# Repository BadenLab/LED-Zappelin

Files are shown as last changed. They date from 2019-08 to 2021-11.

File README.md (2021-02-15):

<p align="right">
<h1 align="center">LED Zappelin'</h1></p>
<h3 align="center">An open source and versatile LED controller for arbitrary spectrum visual stimulation<br>
and optogenetics during 2-photon imaging.</h4>
<p align="center"><h6 align="right">by M.J.Y. Zimmermann, A.M. Chagas, P. Bartel, S. Pop, L.L. Prieto Godino & T. Baden</h6></p>

<br>

This project was published in July 2020 in the journal [HardwareX](https://www.sciencedirect.com/science/article/pii/S2468067220300365)<br>
This project is licensed under the [GNU General Public License v3.0](https://github.com/BadenLab/LED-Zappelin/blob/master/LICENSE)<br>
The hardware is licensed under the [CERN OHL v1.2](https://github.com/BadenLab/LED-Zappelin/blob/master/PCB/LICENSE)

Demo CountPages alpha (https://youtu.be/FhLoFGbbpPo)

***

<h4 align="justify"> Two-photon (2P) microscopy is a cornerstone technique in neuroscience research, but combining this technology with spectrally arbitrary light stimulation can be challenging due to crosstalk between stimulation light and fluorescence detection. To overcome this limitation, we present a simple and low-cost electronic solution based on an ESP32 microcontroller and a TLC5947 LED driver to rapidly time-interleave stimulation and detection epochs during scans. Implemented for less than $100, our design can independently drive up to 24 arbitrary spectrum LEDs to meet user requirements. We demonstrate the utility of our stimulator for colour vision experiments on the in vivo tetrachromatic zebrafish retina and for optogenetic circuit mapping in Drosophila.</h4></p>

***

- [An open and versatile LED controler](#Introduction)
- [A £100 DIY efficient stimulator](https://github.com/BadenLab/LED-Zappelin/blob/master/Bills%20of%20Materials/BOM%20-%20Stimulator.csv)
- [A stimulator for visual neuroscience](#Colour-Vision-Experiment)
- [A stimulator for optogenetics](#Optogenetics-Experiment)
- [A detailed assembly and instruction manual](https://github.com/BadenLab/LED-Zappelin/blob/master/Instruction%20Manual/README.md)
- [A step by step calibration script](https://github.com/BadenLab/LED-Zappelin/blob/master/Instruction%20Manual/Stimulator%20Calibration/Stimulator_Calibration.ipynb)
- [Repository Structure](#Repository-Structure)

***

## Introduction

<p align="justify"> Combining 2P imaging with additional light stimulation – for example for visual stimulation or for driving optogenetic actuators – has remained challenging because the stimulation light can interfere with fluorescence detection. This can result in light artefacts in the image and/or may damage sensitive fluorescence detection equipment (e.g. photomultiplier tubes, PMTs).</p>

<p align="justify">A temporal separation between light stimulation and fluorescence detection, for example during the scan-retrace, can ameliorate these problems.
This problem can be readily solved electronically, for example through use of a microcontroller.</p>

<p align="justify">Here, we present such a solution. Our system can line-synch up to 24 independent LED channels, and can be assembled from off-the-shelf components for substantially below $100. This provides for flexible options of spectrally diverse light stimulation during 2-photon scanning and comfortably provides sufficient power to drive standard optogenetics actuators such as CsChrimson.</p>

<p align="justify">Alongside, we also provided a custom 3D-printed casing, designed suggestions for optically combining LED banks using Thorlabs parts, and an alternative 3D-printed LED holder and microscope chamber. For software control, we provided custom Arduino scripts to flexibly programme stimulation protocols.</p>

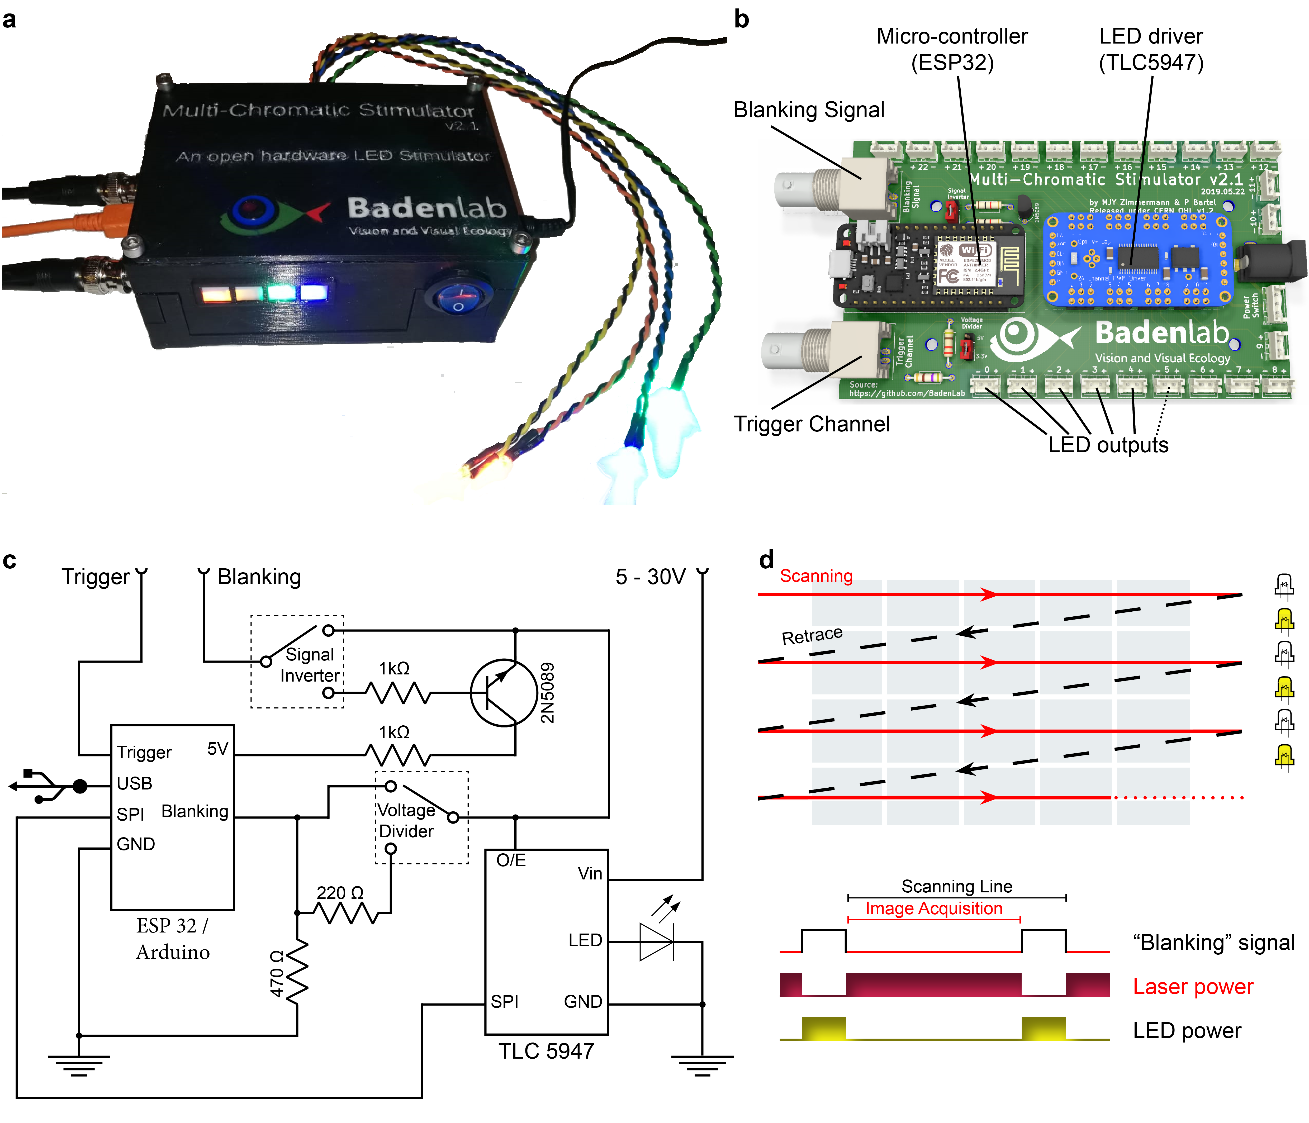
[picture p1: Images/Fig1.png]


<h5 align="justify"> a) A fully assembled stimulator. b) Rendering of the custom-printed circuit board which accommodates the microcontroller, the LED driver and up to 24 LED channels. c) Schematics illustrating the circuit that controls the LED output. The blanking input can be inverted by a switch before reaching the output enable pin on the LED driver (electronically switching off the LEDs) and sending the signal to the micro-controller. A second switch control the blanking signal voltage as it needs to be adapted depending on the logic of the microcontroller used (3.3V for ESP32, 5V for Arduino). The microcontroller controls the LED driver through an SPI connection and send trigger signal output to an external. d) Illustration of the raster scan method described. The “blanking signal” is synchronous with the scanning logic, enabling the LEDs during the scanning mirrors retrace (black) and shutting them off during the acquisition (red), therefore providing temporal separation between stimulation and detection (Modified from (Euler et al. 2019)</h5>

***

<p align="justify">The stimulator runs synchronous to the recording system using TTL triggers. TTL signals correspond to scanning mirror retrace periods and are used to turn ON and OFF LEDs, thus avoiding swamping the PMTs by stimulation light.

<p align="justify">On the PCB, we incorporated a signal inverter which can be enabled through a jumper (see below) and that can modulated the TTL signal sign. This customisable option thus offers the possibility for a single design to be easily adapted to multiple imaging systems.</p>

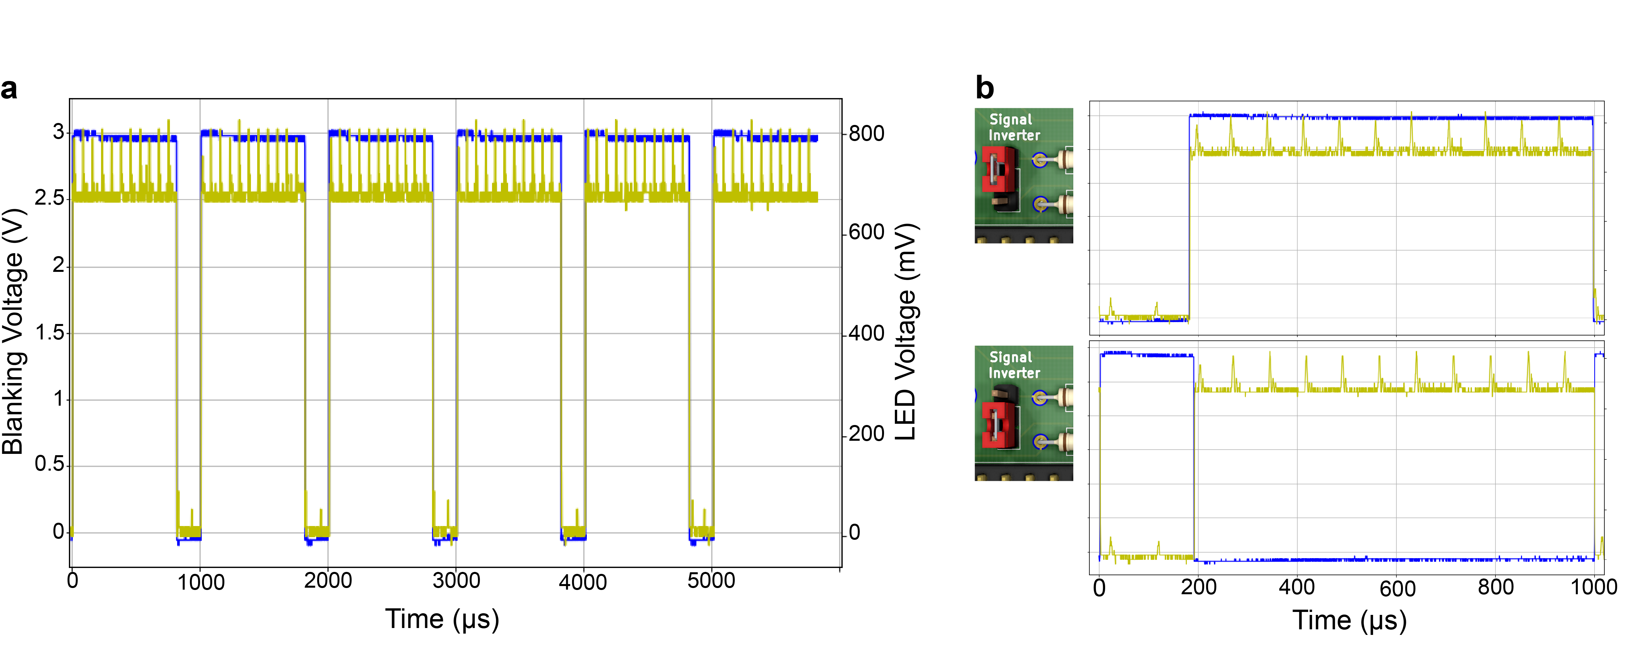
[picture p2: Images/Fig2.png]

<h5 align="justify"> a) Oscilloscope reading of the blanking signal (blue) efficiently switching off an LED (yellow). The blanking is operated here without noticeable delay. b) Same as a), showing for a 1ms scanning cycle, the two possible configurations for the blanking signal input, with a low (top) and a high (bottom) blanking signal input respectively for an inverted and original signal input. </h5>

***

<p align="justify"> The use of a dedicated constant current LED driver tends to improve LED stability over time as well as its life span. Such driver ensures that the current drawn by the LED never leads to thermal runaways that might cause irreversible damage. This is particularly essential for short wavelength LEDs which tend to rapidly decay, thus necessitating regular recalibration or replacement. </p>

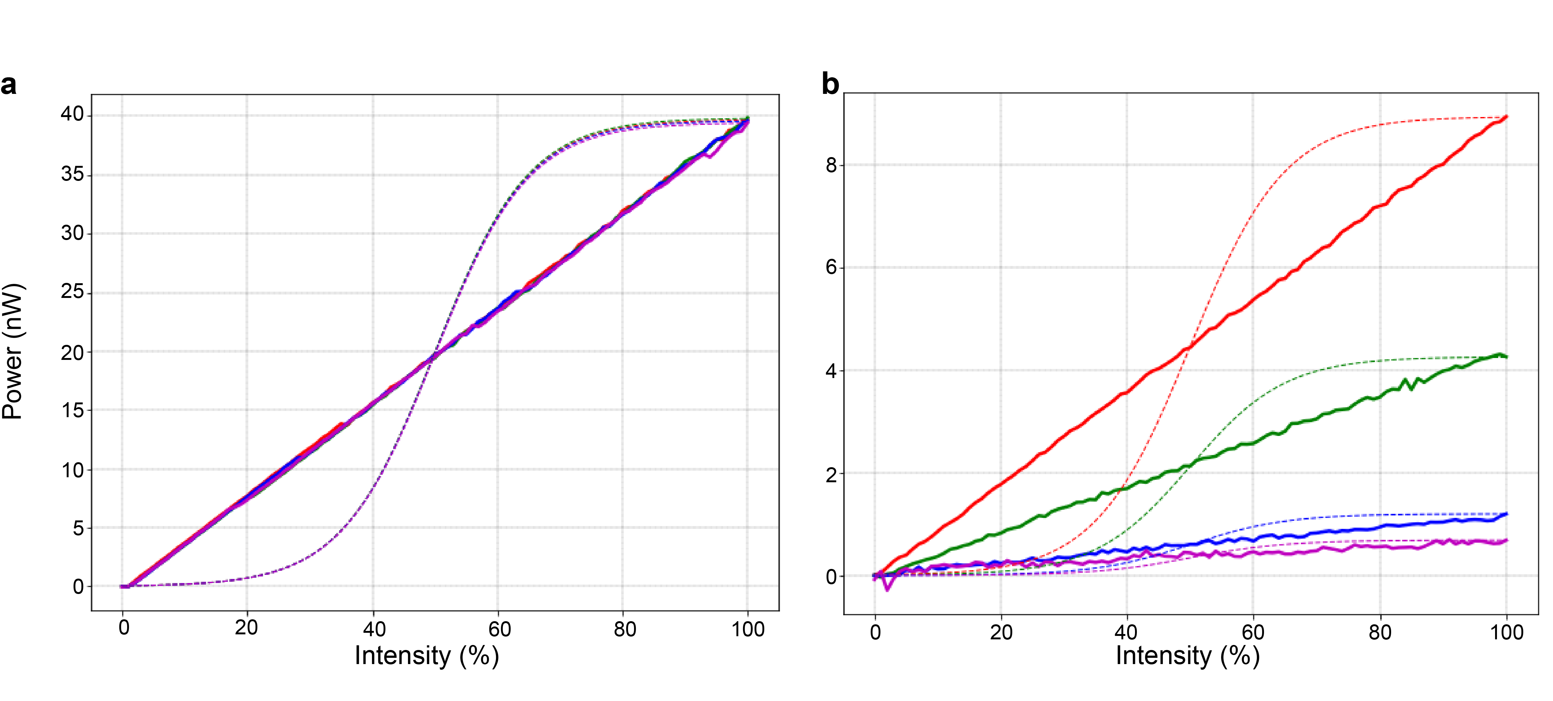
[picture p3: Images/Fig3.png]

<h5 align="justify">  a) Power recording of a 4 LED system using the TLC5947 (solid lines) and their expected brightness if directly controlled by a microcontroller (dashed lines). All LEDs have been set up to the same power (40nW), with equal max intensities values in the Arduino code. b) Same as a) but with LEDs set up at different max intensities in the Arduino code. Here the linearity of the LED intensity output remains constant. </5>

***

## Colour Vision Experiment

<p align="justify">We used LED Zappelin' for studying the retinal processing of the tetrachromatic zebrafish retina in response to multichromatic signal.
Here we selected four LEDs that match the peak sensitivities of each cone opsins of our model.
We chose LEDs and band pass filters in such manner that the stimulating light and the detection bands do not overlap as much as possible. However a temporal separation is still necessary to avoid some overlapping and any light artifact. </p>

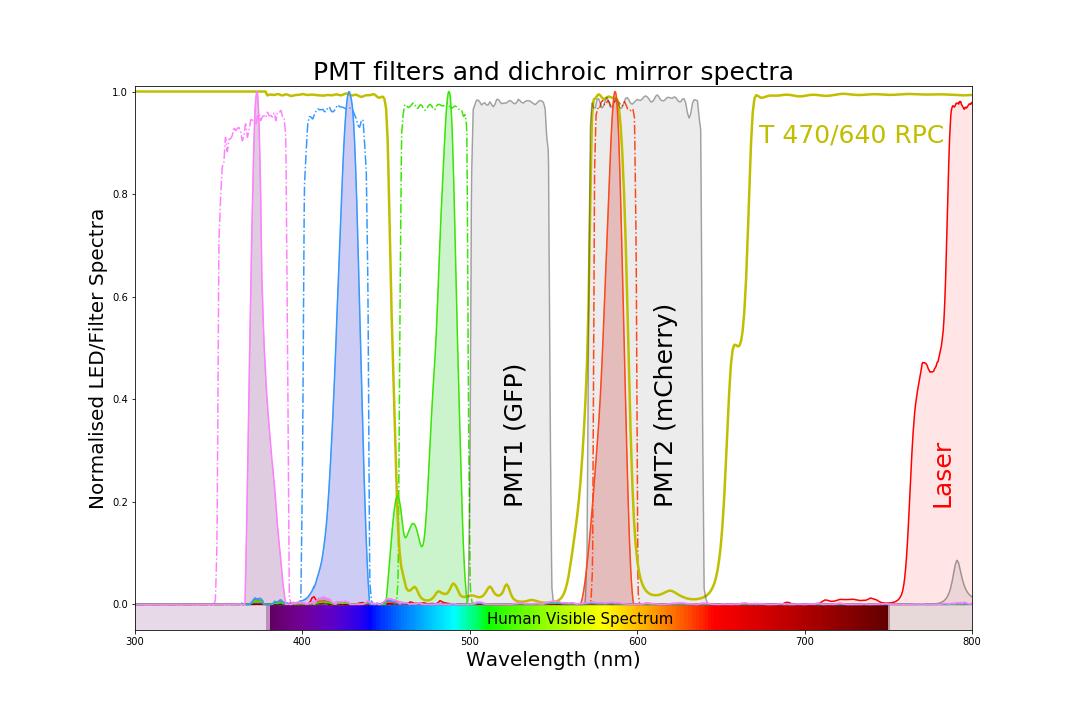
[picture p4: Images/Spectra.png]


 We recorded light-driven calcium signals under 2-photon from [retinal bipolar cells in vivo in the tetrachromatic larval zebrafish](https://github.com/BadenLab/LED-Zappelin/blob/master/References/Zimmermann%202018%20-%20Zebrafish%20Differentially%20Procces%20Colour%20across%20Visual%20Space%20to%20Match%20Natural%20Scenes.pdf). We used a transgenic line expressing a genetically encoded biosensors for calcium at the  bipolar cell synaptic terminals level (ctbp2:SyGCaMP6)  within the inner plexiform layer (IPL).

Following [established protocols](https://github.com/BadenLab/LED-Zappelin/blob/master/References/Denk%202009%20-%20Eyecup%20Scope%20-%20optical%20recordings%20of%20light%20stimulus-evoked%20fluorescence%20signals%20in%20the%20retina.pdf), we used a Sutter MOM microscope where light stimulation is displayed through the objective directly onto the fish retina along with the laser excitation. Fluorescence is also collected through the objective as well as from below the stage (not shown).

We presented full field steps of red, green, blue and UV light to the fish eye (respectively 567, 480, 420 and 365nm), and recorded evoked calcium signals as a readout of synaptic activity. We observed spectrally different tunings from distinct bipolar cell terminals  without detectable stimulus artefact across the scan.

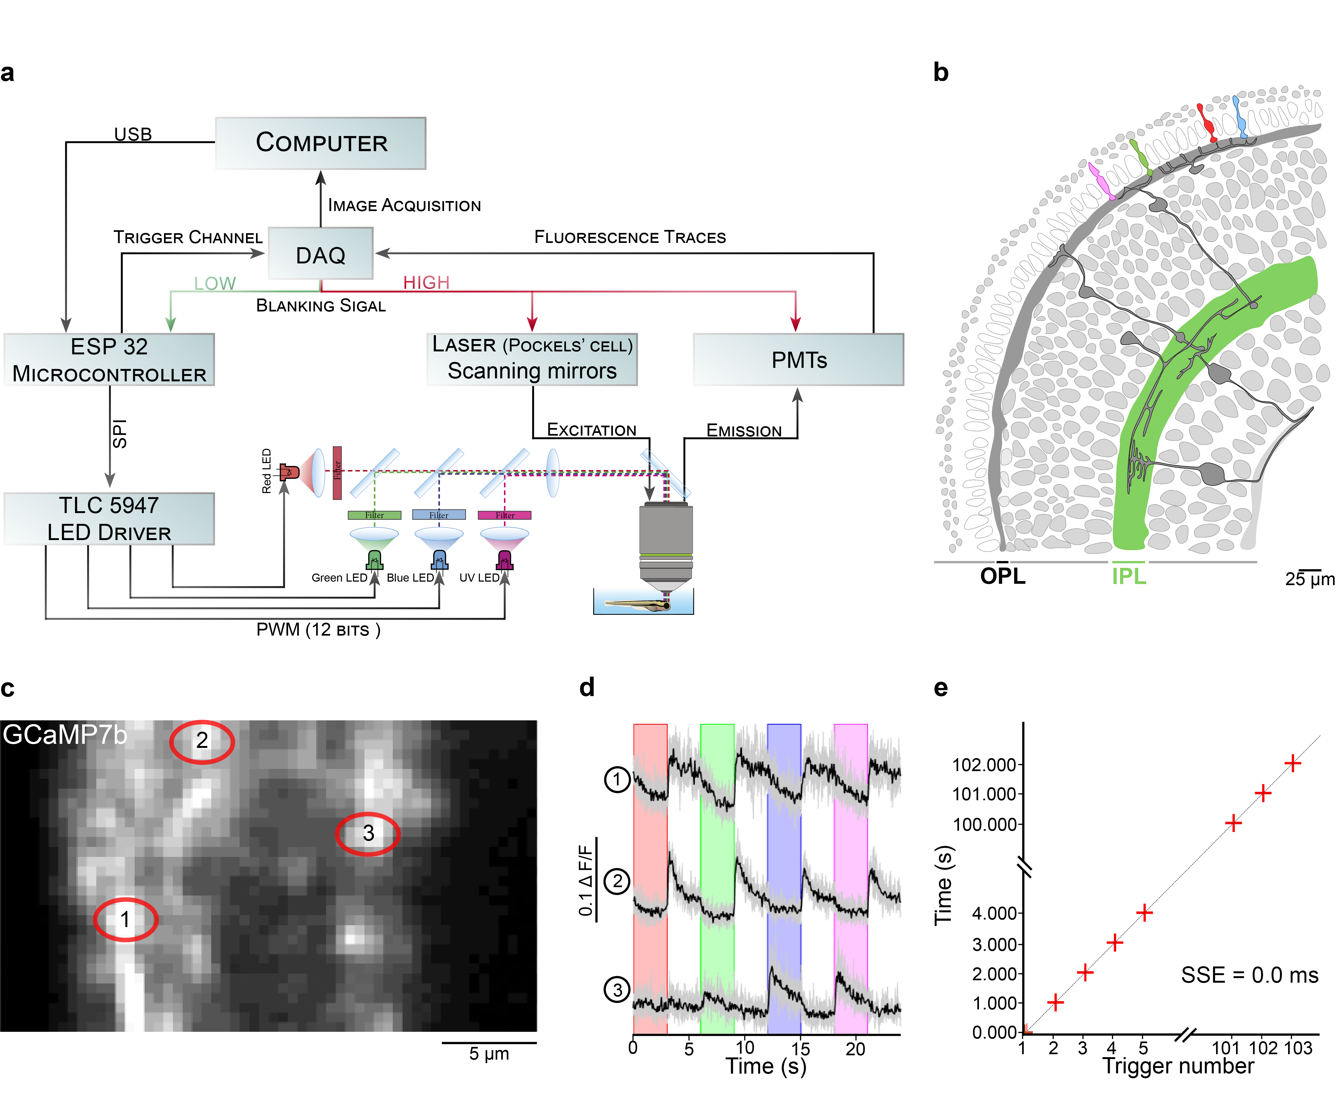
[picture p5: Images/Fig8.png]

<h5 align="justify"> a) Overview of the setup described for the visual stimulation experiment performed on the tetrachromatic zebrafish. b) Drawing of the larval zebrafish retina highlighting the IPL. c) 2 photon scan field of the IPL with regions-of-interest marked by red circles. The 64x32 pixel image was obtained by at 1ms scan rate. d) Ca²⁺ traces (mean traces in black, n=5 trials in grey) in response to consecutive red, green, blue and UV On/Off flashes. e) Trigger timing recorded by the DAQ highlighting its accuracy over time with a precision of 0.1µs. t(n+1) = t(n) + T, where “t” is the recorded trigger time and “T” the trigger period. </5>

***

## Optogenetics Experiment

In addition to colour vision experiments, LED Zappelin' is well suited for optogenetic manipulations.

<p align="justify">Here we illustrate this application in Drosophila larvae, were we recorded brain-wide calcium signals under 2P in response to optogenetic stimulation of all olfactory sensory neurons (OSNs).  We expressed the red-shifted channel rhodopsin CsChrimson OSNs and the genetically encoded calcium indicator GCaMP6s pan-neuronally by using larvae with the genotype: elav-Gal4;UAS-GCaMP6s/Orco-LexA;LexAOp-CsChrimson.</p>

We placed first instar larvae under a custom-made 2P microscope in a [3D-printed optogenetics LED chamber](https://github.com/BadenLab/LED-Zappelin/blob/master/3D%20Design/Optogenetics%20Components).
Red light stimulation was delivered from around the sides of the recording chamber and GCaMP6s fluorescence intensity was collected by two detectors one through the objective lens, and a sub-stage PMT.
We presented full field illumination steps of 615 nm light lasting 0.5 s and an inter-stimulus interval of either 3 s (b) or 10 s (c).

<p align="justify">We observed robust stimulus-evoked activity in the primary olfactory sensory centres of the larval brain, the antennal lobes (red outlines). Similarly to colour vision experiments, we detected no light artefact. </p>

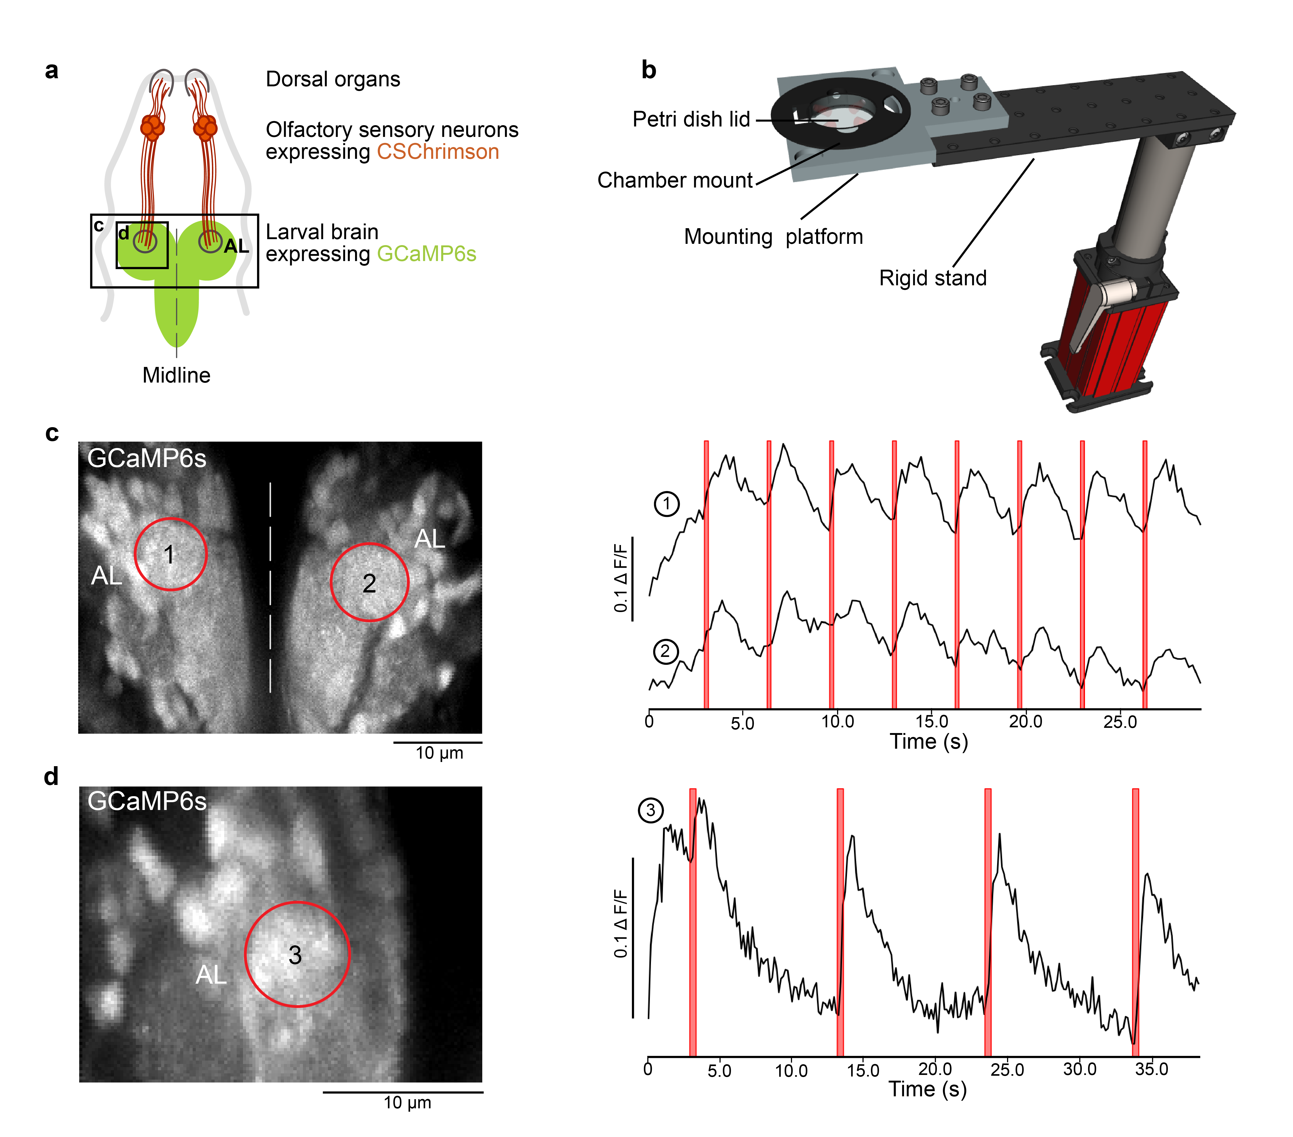
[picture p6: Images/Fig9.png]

<h5 align="justify">  a) Schematic of a fruit fly first instar larval head expressing the red-shifted channel rhodopsin CsChrimson in olfactory sensory neurons and GCaMP6s in all neurons. b) Rendering of the experimental setup: The mounting chamber is placed in a 3D-printed holder, screwed onto a rigid stand (ThorLabs).  c),d)  2 photon scan field of the larval brain with antennal lobes marked by red circles (left) and Ca²⁺ traces in response to red flashes (right). c. Stimulation duration = 0.5 s, inter-stimulus interval = 3 s, image dimensions = 256 x 230, scan rate = 1081 Hz, frame rate = 4.7 Hz. d) Stimulation duration = 0.5 s, inter-stimulus interval = 10 s, image dimensions = 256 x 170, scan rate = 1077Hz, frame rate = 6.34 Hz. </h5>

***
## Repository structure

```
├───3D Designs                                Contains printed parts for the stimulator and optical components
│   ├───Optical Components
|   |   ├───STL renderings                    - Printing files
|   |   └───SCAD files                        - SCAD files to be modified if need be
│   ├───Optogenetics Components
|   |   ├───STL renderings                    - Printing files
|   |   └───SCAD files                        - SCAD files to be modified if need be
│   └───Stimulator
|       ├───STL renderings                    - Printing files
|       └───SCAD files                        - SCAD files to be modified if need be
|
├───Arduino Code                              Stimulator Code
|   ├───Stimulator Code                       - Adaptable C+ code for running the stimulator
|   └───LED driver library                     - Library to run the TLC 5947
|
├───Bill of Materials                         List of necessary components and retailer suggestions
|
├───Datasheets                                - Contains all technical sheet for:
|   ├───Optical Components                    - ...LEDs, Filters, Dichroic Mirrors used in the presented example
|   ├───Stimulator                            - ...micro-controller and LED driver
|   └───Spectrometer                          - ...device used for calibration
|
├───Images                                    Image repository
|
├───Instruction Manual                        Detailed manual to assemble and calibrate the stimulator
|   └───Stimulator Calibration                - Contains calibration recordings and the adaptable jupyter notebook script to calibrate the stimulator
|       ├───Arduino Calibration Code          - Sequence used for the calibration
|       ├───Calibration Figures               - Illustration from calibration measurements
|       ├───Filters                           - Filters and dicroic mirrors spectra
|       ├───Powermeter Recording              - Recording of the calibration sequence
|       ├───Spectrometer Recording            - Recording of the calibration sequence
|       └───Stimulator Calibration            - iPython Jupyter Notebook script for calibration
|
├───PCB                                       KiCad and Gerber files to modified and generate PCB for:
│   ├───Potentiometer mounts                  - ...trimmer potentiometers that set the LED maximum brightness
│   └───Stimulator                            - ...the stimulator itself
|
└───References                                Publication used to design and conceive this model

```

***

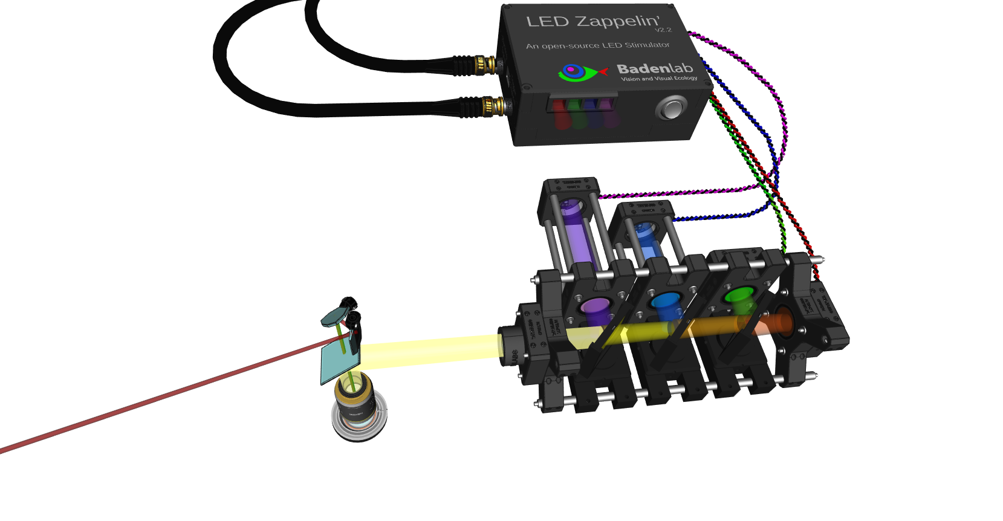
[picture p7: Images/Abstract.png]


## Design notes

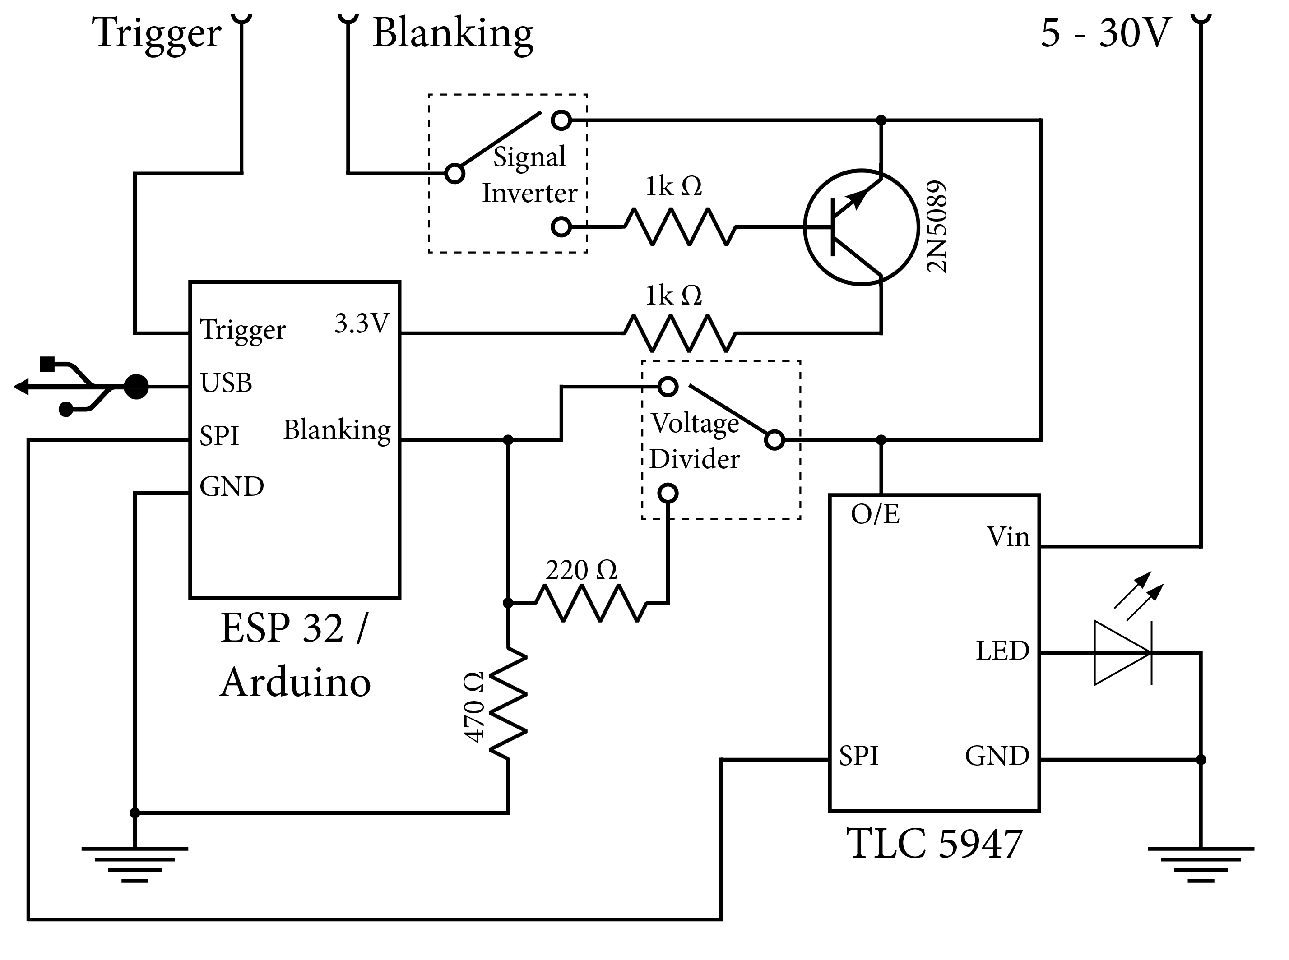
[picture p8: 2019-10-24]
Images/Schematics.png

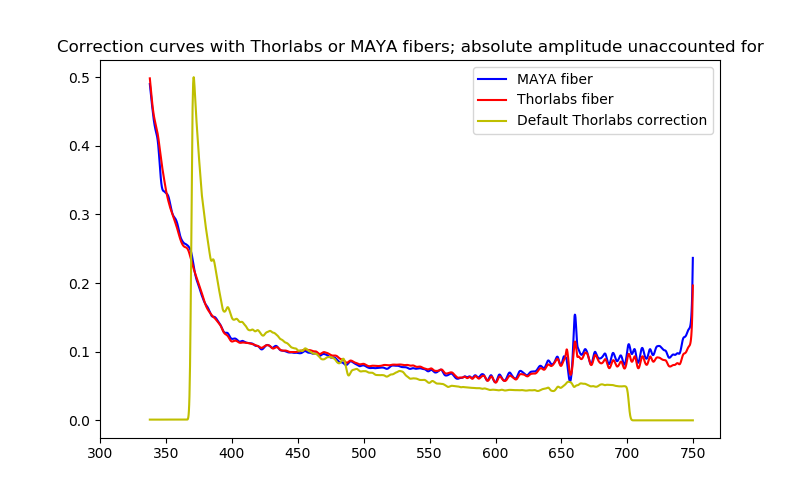
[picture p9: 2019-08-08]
Instruction Manual/Stimulator Calibration/Spectrometer_Recording/Spectrometer Correction Curves/Correction_curves.png

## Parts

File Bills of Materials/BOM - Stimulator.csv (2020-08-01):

Name | Manufacturer | Order ID | Retailer | Quantity | Observation 1 | Observation 2 | Suggested URL | Cost
Adafruit Huzzah32 - ESP32 Feather | Adafruit | 3405 | Adafruit | 1 | Development Board | Easier to order it with header pins soldered | https://www.adafruit.com/product/3405 | £17
Adafruit TLC5947 | Adafruit | 1429 | Adafruit | 1 | LED Driver |  | https://www.adafruit.com/product/1429 | £12
BNC coaxial connectors | TE Connectivity | 1-1337542-0 | Farnell | 2 | Electronics | Right angle jacks, 50ohm | https://uk.farnell.com/greenpar-te-connectivity/1-1337542-0/rf-coaxial-bnc-right-angle-jack/dp/1020954?st=bnc%20pcb%20mout | £3.70
2 way JST Female Connector Housing | RS Online | 820-1611 | JST | 8 | Electronics |  | https://uk.rs-online.com/web/p/pcb-connector-housings/8201611/ | £3.80
3 way JST Female Connector Housing | RS Online | 820-1614 | JST | 1 | Electronics |  | https://uk.rs-online.com/web/p/pcb-connector-housings/8201614/ | £1.90
4 way JST Female Connector Housing | RS Online | 820-1618 | JST | 2 | Electronics |  | https://uk.rs-online.com/web/p/pcb-connector-housings/8201618/ | £1.90
2 way JST PCB header | RS Online | 820-1554 | JST | 8 | Electronics |  | https://uk.rs-online.com/web/p/pcb-headers/8201554/ | £3.80
3 way JST PCB header | RS Online | 820-1557 | JST | 1 | Electronics |  | https://uk.rs-online.com/web/p/pcb-headers/8201557/ | £1.90
4 way JST PCB header | RS Online | 820-1551 | JST | 2 | Electronics |  | https://uk.rs-online.com/web/p/pcb-headers/8201551/ | £1.90
JST Crimp Connector Wire | RS Online | 01SHXSXH-26L 150 | RS | 15 | Electronics |  | https://uk.rs-online.com/web/p/products/8201548/ | £10.00
3 mm LED | Digikey | 350-1557-ND | Digikey | 4 | Electronics | 3mm round, tht | https://www.digikey.com/product-detail/en/dialight/5219210F/350-1557-ND/808955 | £2
Mount for 3 mm LED | Digikey | 67-1330-ND | Digikey | 4 | Electronics | 3mm panel mount | https://www.digikey.com/products/en?keywords=67-1330-ND | £1
Mount for 5 mm LED | Digikey | 67-1332-ND | Digikey | 4 | Electronics | 5mm panel mount | https://www.digikey.com/product-detail/en/lumex-opto-components-inc/SSH-LX5091/67-1332-ND/144810 | £1
Rocker LED switch |  |  | Ebay | 1 | Electronics | Round Switch / 3 pins | https://www.ebay.co.uk/p/Blue-On-off-Lighted-LED-Round-Rocker-Switch-Car-Dashboard-Dash-SPST-12v/1942302409?iid=262042885084&chn=ps | £2.50
220 Ohms Resitor | RS Online | 707-7612 | RS | 1 | Electronics | Through hole | https://uk.rs-online.com/web/p/through-hole-fixed-resistors/7077612/ | £1.16
470 Ohms Resitor | RS Online | 707-7647 | RS | 1 | Electronics | Through hole | https://uk.rs-online.com/web/p/through-hole-fixed-resistors/7077647/ | £1.16
10 kOhms Trimmer Potentiometer | TT Electronics | 89PR10KLF | Farnell | 4 | Electronics | Through Hole | https://uk.farnell.com/bi-technologies-tt-electronics/89pr10klf/trimmer-resistor/dp/1653213?st=trimmer%20potentiometer | £5.95
PCB socket | Samtec | SSW-116-02-G-S | RS | 6 | Electronics | 1 row, 15 pin | https://uk.rs-online.com/web/p/pcb-sockets/7655795/ | £3
2.1 mm right angle DC socket | RS Online | 884-0957 | RS | 1 | Electronics | 2.1 mm right angle | https://uk.rs-online.com/web/p/dc-power-sockets/8840957/ | £1
distinc colour wires | RS Online | 331-862 | RS | 100 cm | Electronics | 20 AWG | https://uk.rs-online.com/web/p/hookup-equipment-wire/0331862/ | £5
Cable shrink | RS Online | 170-6377 | RS | 20 cm | Electronics | Shrunk diameter 1.2 mm | https://uk.rs-online.com/web/p/heat-shrink-cold-shrink-sleeves/1706377/ | £1.58
M3 x 10mm screw | RS Online | 660-4636 | RS | 4 | Mechanical | M3 x 10 Hex socket cap | https://uk.rs-online.com/web/p/socket-screws/6604636/ | £4
M3 nut | RS Online | 122-4400 | RS | 4 | Mechanical | M3 nuts | https://uk.rs-online.com/web/p/hex-nuts/1224400/ | £4
M4 x 50mm Hex Socket Cap Screws | RS Online | 304-4592 | RS | 4 | Mechanical | M4 x 50 | https://uk.rs-online.com/web/p/socket-screws/3044592/ | £4
M4 nut | RS Online | 189-579 | RS | 4 | Mechanical | M4 nuts | https://uk.rs-online.com/web/p/hex-nuts/0189579/ | £4
 |  |  |  |  |  |  |  | £101

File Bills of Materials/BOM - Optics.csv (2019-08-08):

Name | Part id | Manufacturer | order id | Retailer | Quantity | obs1 | obs2 | obs3 | URL
Red LED | B5B-434-TY | Roithner |  | Roitner | 1 | LED |  | 5mm | http://www.roithner-laser.com/led_diverse.html
Green LED | RLS-5B475-S | Roithner |  | Roitner | 1 | LED |  | 5mm | http://www.roithner-laser.com/led_diverse.html
Blue LED | VL415-5-15 | Roithner |  | Roitner | 1 | LED |  | 5mm | http://www.roithner-laser.com/led_diverse.html
UV LED | XSL-365-5E | Roithner |  | Roitner | 1 | LED |  | 5mm | http://www.roithner-laser.com/led_diverse.html
Red LED Filter | FF01-586/20 BrightLine HC | Semrock | F39-587 | AHF | 1 | Band Pass Filter |  | 22.9mm | https://www.ahf.de/en/products/spectral-analysis-photonic/optical-filters/individual-filters/bandpass-filters/500-599-nm/2098/586/20-brightline-hc?c=499
Green LED Filter | ET 480/40 | Chroma | F49-480 | AHF | 1 | Band Pass Filter |  | 22.9mm | https://www.ahf.de/en/products/spectral-analysis-photonic/optical-filters/individual-filters/bandpass-filters/400-499-nm/2598/480/40x-et-bandpass
Blue LED Filter | ET 420/40 | Chroma | F47-420 | AHF | 1 | Band Pass Filter |  | 22.9mm | https://www.ahf.de/en/products/spectral-analysis-photonic/optical-filters/individual-filters/bandpass-filters/400-499-nm/2370/420/40-et-bandpass
UV LED Filter | FF01-370/36 BrightLine HC | Semrock | F39-370 | AHF | 1 | Band Pass Filter |  | 22.9mm | https://www.ahf.de/en/products/spectral-analysis-photonic/optical-filters/individual-filters/bandpass-filters/200-399-nm/1985/370/36-brightline-hc
U/RGB Beamsplitter | T 400 LP | Chroma | F79-100 | AHF | 1 | Dichroic Mirror |  | 25.5X36X1mm | https://www.ahf.de/en/products/spectral-analysis-photonic/optical-filters/dichroic-beamsplitters/beamsplitters-for-epi-fluorescence/standard-beamsplitters/lon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
B/RG Beamsplitter | T 450l LPXR | Chroma | F48-450 | AHF | 1 | Dichroic Mirror |  | 25.5X36X1mm | https://www.ahf.de/en/products/spectral-analysis-photonic/optical-filters/dichroic-beamsplitters/beamsplitters-for-epi-fluorescence/standard-beamsplitters/lon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
G/R Beamsplitter | H 560 LPXR | AHF | F48-559 | AHF | 1 | Dichroic Mirror |  | 25.5X36X1mm | https://www.ahf.de/en/products/spectral-analysis-photonic/optical-filters/dichroic-beamsplitters/laser-beamsplitters/longpass-laser-beamsplitters/single/2517/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
50mm Lens | ACA254-050-A | ThorLabs | ACA254-050-A | ThorLabs | 1 | 350-750 nm |  | 25.4 * 13.3mm | https://www.thorlabs.com/thorproduct.cfm?partnumber=ACA254-050-A
Cage System Right-Angle Adapter | LCP30 | ThorLabs | LCP30 | ThorLabs | 3 | Cage Assembly |  | 60mm to 30mm | https://www.thorlabs.com/thorproduct.cfm?partnumber=LCP30
Cage Plate Adapter | LCP02/M | ThorLabs | LCP02 | ThorLabs | 2 | Cage Assembly |  | 30mm to 60mm | https://www.thorlabs.com/thorproduct.cfm?partnumber=LCP02/M
Cage Plate | CP02T/M | ThorLabs | CP02T/M | ThorLabs | 4 | Cage Assembly |  | 30mm x 0.5" threaded | https://www.thorlabs.com/thorproduct.cfm?partnumber=CP02T/M
Assembly Rod | ER8 | ThorLabs | ER8-P4 | ThorLabs | 4 | Cage Assembly |  | 6mmx8" | https://www.thorlabs.com/thorproduct.cfm?partnumber=ER8-P4
Assembly Rod | ER6 | ThorLabs | ER6-P4 | ThorLabs | 4 | Cage Assembly |  | 6mmx6" | https://www.thorlabs.com/thorproduct.cfm?partnumber=ER6-P4
Assembly Rod | ER4 | ThorLabs | ER4-P4 | ThorLabs | 4 | Cage Assembly |  | 6mmx4" | https://www.thorlabs.com/thorproduct.cfm?partnumber=ER4-P4
Assembly Rod | ER2 | ThorLabs | ER2-P4 | ThorLabs | 4 | Cage Assembly |  | 6mmx2" | https://www.thorlabs.com/thorproduct.cfm?partnumber=ER2-P4
Assembly Rod | ER1 | ThorLabs | ER1-P4 | ThorLabs | 4 | Cage Assembly |  | 6mmx1" | https://www.thorlabs.com/thorproduct.cfm?partnumber=ER1-P4
Mounting Post | P10 | ThorLabs | P10 | ThorLabs | 1 | Cage Assembly |  | 1/4" x 10" | https://www.thorlabs.com/thorproduct.cfm?partnumber=P10
Base Adapter | PB4 | ThorLabs | PB4 | ThorLabs | 1 | Cage Assembly |  | 1/4" Thread | https://www.thorlabs.com/thorproduct.cfm?partnumber=PB4
Cage Clamp | CH1560/M | ThorLabs | CH1560/M | ThorLabs | 1 | Cage Assembly |  | 1.5" Post | https://www.thorlabs.com/thorproduct.cfm?partnumber=CH1560/M

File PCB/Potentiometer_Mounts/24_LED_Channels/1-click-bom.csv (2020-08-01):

References | Qty | Description | Manufacturer | MPN | Manufacturer_1 | MPN_2 | Manufacturer_3 | MPN_4 | Manufacturer_5 | MPN_6 | Manufacturer_7 | MPN_8 | Digikey | Mouser | RS | Newark | Farnell
RV1 | 4 | 10 kOhms Trimmer Potentiometer | Farnell | 89PR10KLF |  |  |  |  |  |  |  |  |  |  |  |  | 89PR10KLF
J1 | 2 | 4 way JST Female Connector Housing | RS Pro | 820-1618 |  |  |  |  |  |  |  |  |  |  | 820-1618
J2 | 2 | 4 way JST PCB header | RS Pro | 820-1551 |  |  |  |  |  |  |  |  |  |  | 820-1551

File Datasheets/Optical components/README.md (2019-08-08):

<p align="right">

This project is licensed under the [GNU General Public License v3.0](https://github.com/MaxZimmer/Multi-Chromatic-Stimulator/blob/master/LICENSE)

***



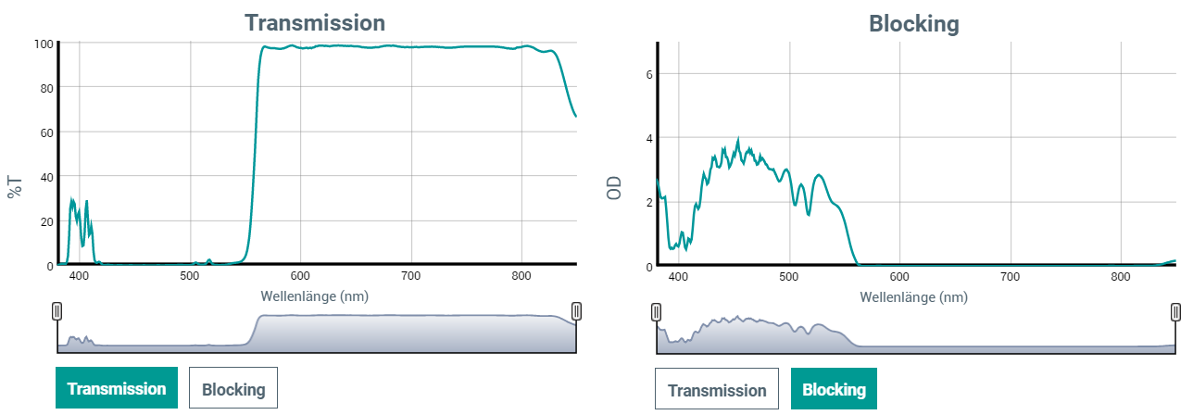
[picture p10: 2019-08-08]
Datasheets/Optical components/Dichroic Mirrors/T 560 LPXR/T 560 LPXR.png

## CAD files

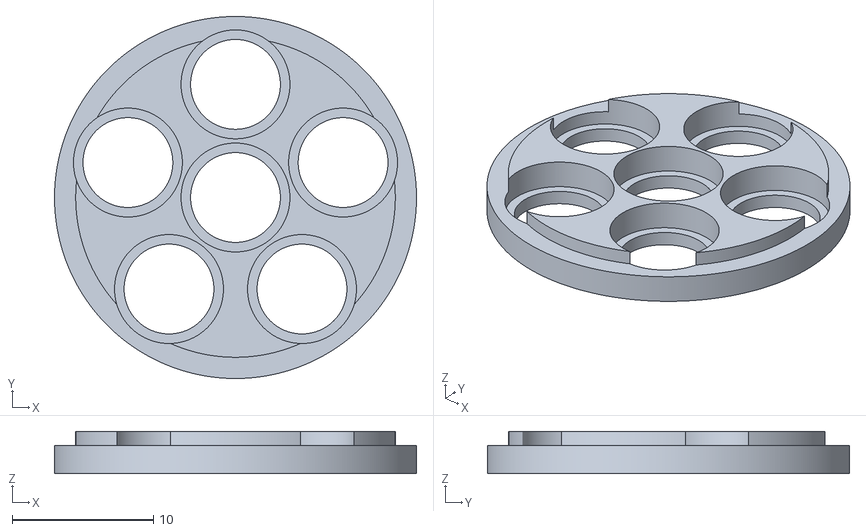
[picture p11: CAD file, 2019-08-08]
3D Designs/Optical Components/STL Files/6_LED_Holder.stl
25.6 x 25.6 x 3.00

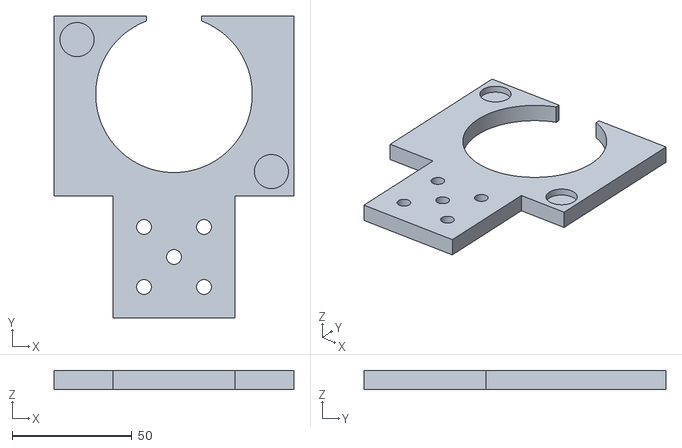
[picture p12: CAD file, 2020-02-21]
3D Designs/Optogenetics Components/STL Files/OptoChamber - Plaform mount.stl
100.0 x 125.8 x 8.00

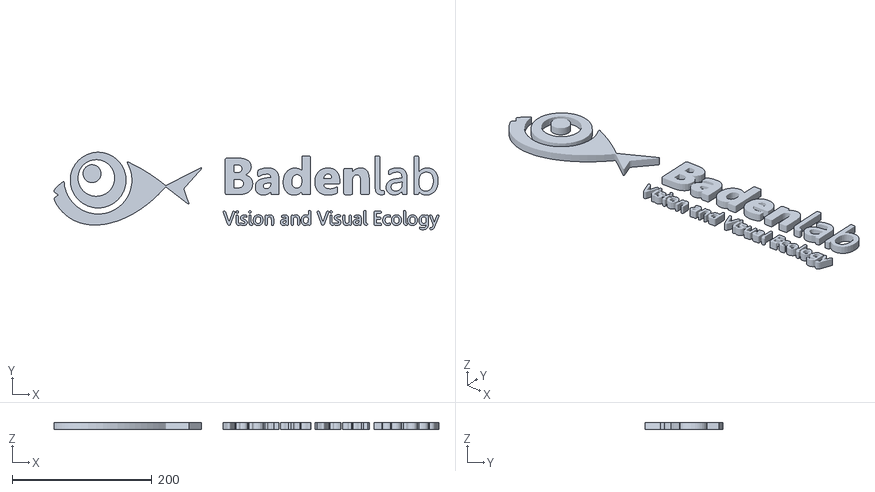
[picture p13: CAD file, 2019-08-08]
3D Designs/Stimulator/Logo/Badenlab_logo.stl
550.3 x 111.0 x 10.0

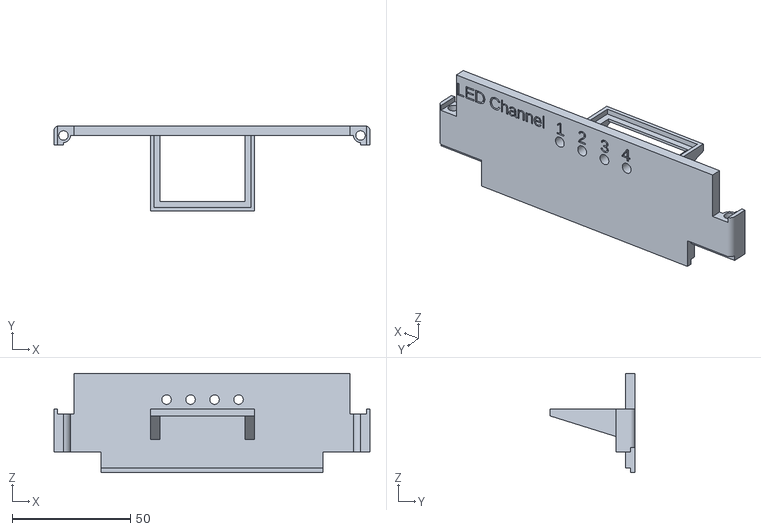
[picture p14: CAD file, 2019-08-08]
3D Designs/Stimulator/STL Files/Back.stl
133.8 x 36.0 x 42.0

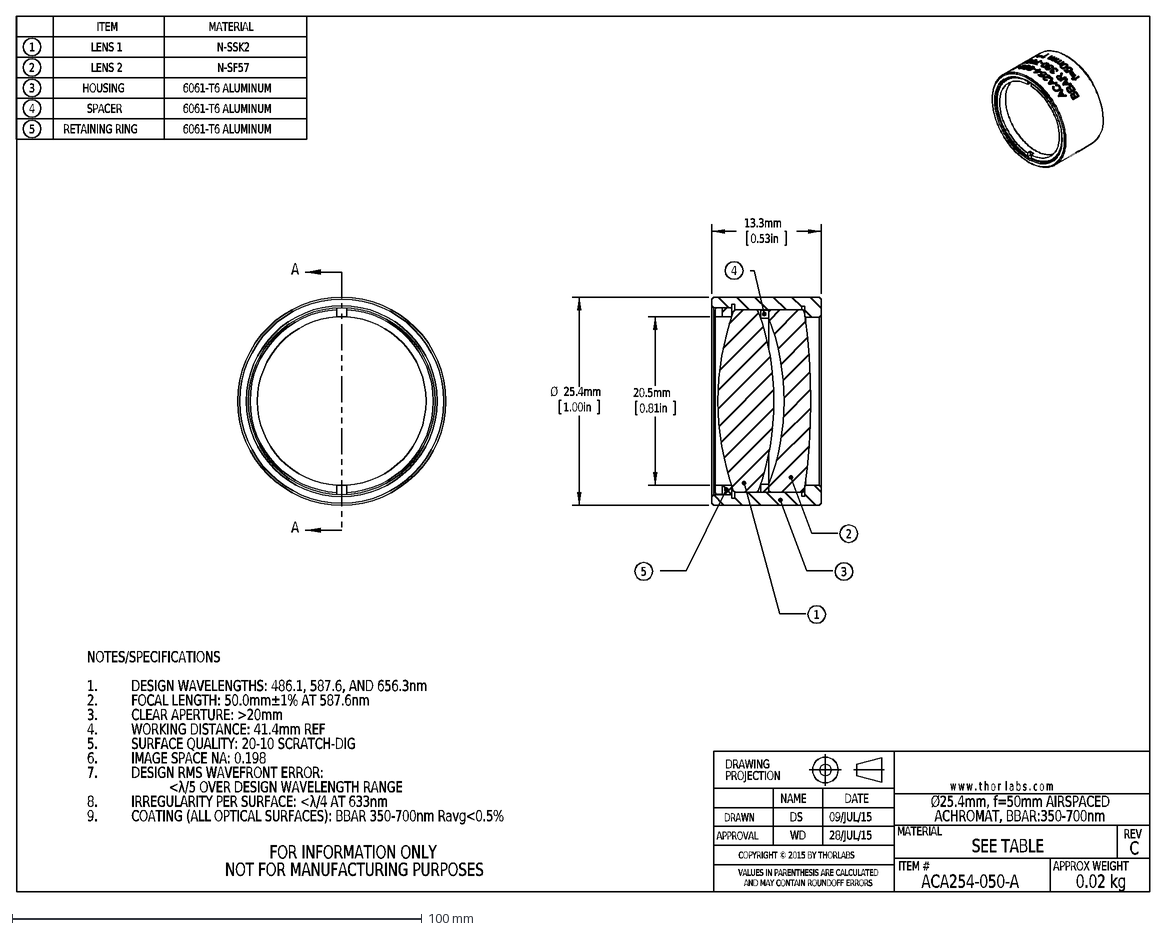
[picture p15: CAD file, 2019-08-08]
Datasheets/Optical components/Optics/50mm Achromatic Doublet lens/ACA254-050-A-AutoCADDXF.dxf
C
ACA254-050-A
MATERIAL
DRAWN
APPROVAL
REV
DS
WD
09/JUL/15
DATE
28/JUL/15
w w w . t h o r l a b s . c o m
ITEM #
APPROX WEIGHT
SEE TABLE
0.02 kg
VALUES IN PARENTHESIS ARE CALCULATED
AND MAY CONTAIN ROUNDOFF ERRORS
DRAWING
PROJECTION
NAME
FOR INFORMATION ONLY
NOT FOR MANUFACTURING PURPOSES
Ø25.4mm, f=50mm AIRSPACED
ACHROMAT, BBAR:350-700nm
COPYRIGHT © 2015 BY THORLABS
NOTES/SPECIFICATIONS
DESIGN WAVELENGTHS: 486.1, 587.6, AND 656.3nm
1.
FOCAL LENGTH: 50.0mm±1% AT 587.6nm
2.
CLEAR APERTURE: >20mm
3.
WORKING DISTANCE: 41.4mm REF
4.
SURFACE QUALITY: 20-10 SCRATCH-DIG
5.
IMAGE SPACE NA: 0.198
6.
DESIGN RMS WAVEFRONT ERROR:
7.
<λ/5 OVER DESIGN WAVELENGTH RANGE
IRREGULARITY PER SURFACE: <λ/4 AT 633nm
8.
COATING (ALL OPTICAL SURFACES): BBAR 350-700nm Ravg<0.5%
9.
ITEM
1
LENS 1
N-SSK2
2
LENS 2
N-SF57
3
HOUSING
6061-T6 ALUMINUM
4
SPACER
5
RETAINING RING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

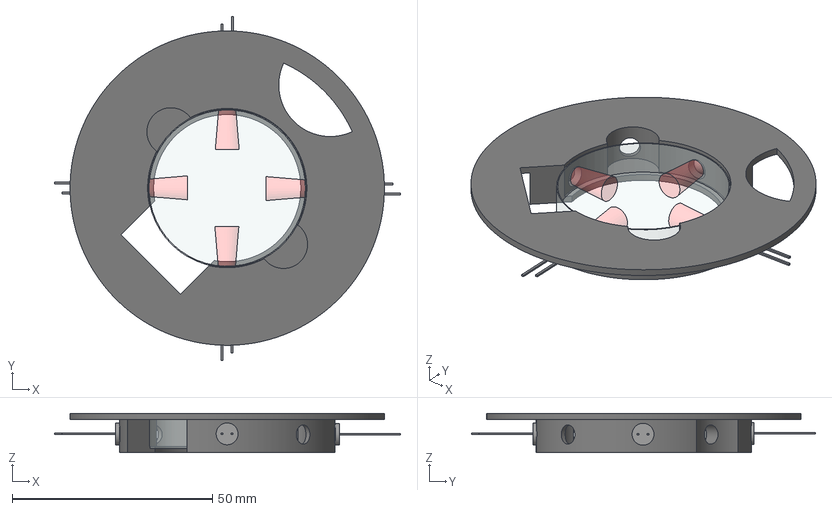
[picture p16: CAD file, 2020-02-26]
Images/FreeCAD renderings/Optogenetics - Mounting Chamber 2.FCStd
86.4 x 85.8 x 9.75 mm
LED 3mm (Red)
LED 3mm (Red)002
LED 3mm (Red)003
LED 3mm (Red)005
OptoChamber - version2

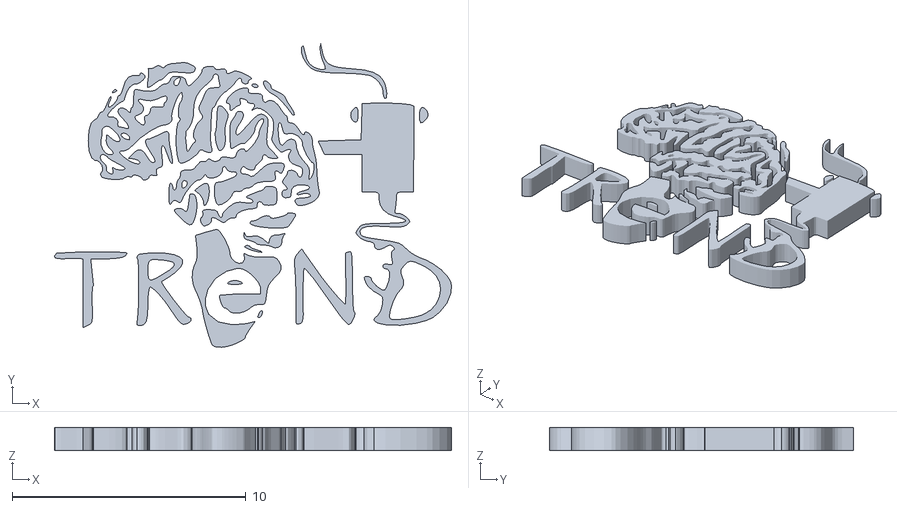
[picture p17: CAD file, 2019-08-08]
Images/Logo/Trend.stl
17.0 x 13.0 x 1.00

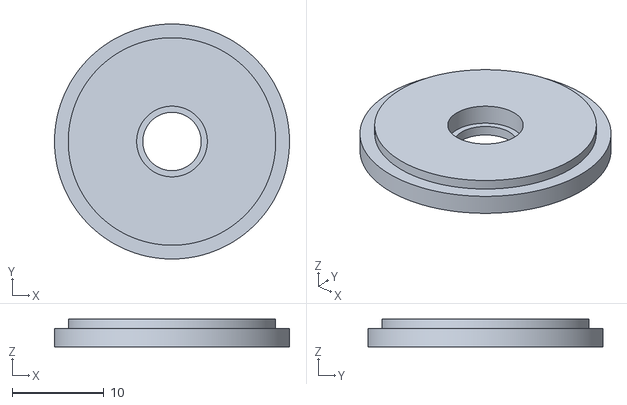
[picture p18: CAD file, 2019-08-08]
3D Designs/Optical Components/STL Files/1_LED_Holder.stl
25.6 x 25.6 x 3.00

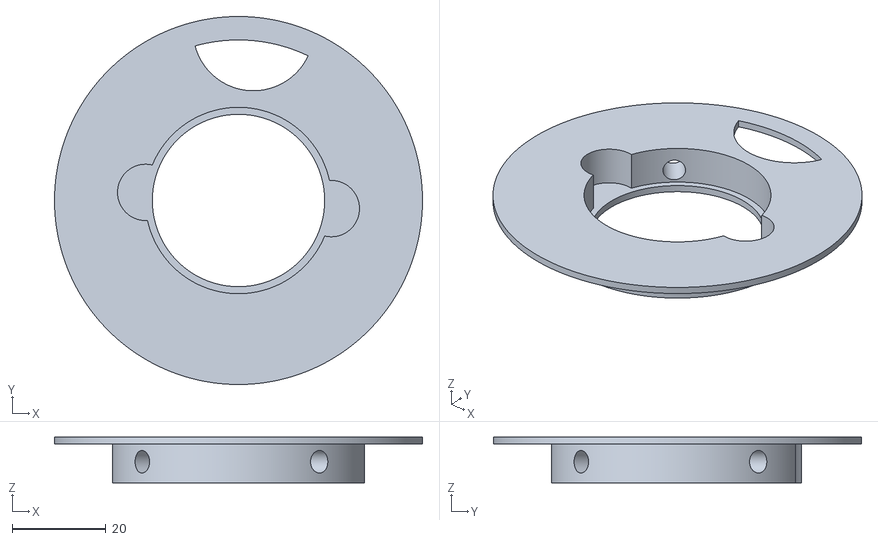
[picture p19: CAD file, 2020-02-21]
3D Designs/Optogenetics Components/STL Files/OptoChamber - RC-40HP version.stl
78.4 x 78.4 x 9.75

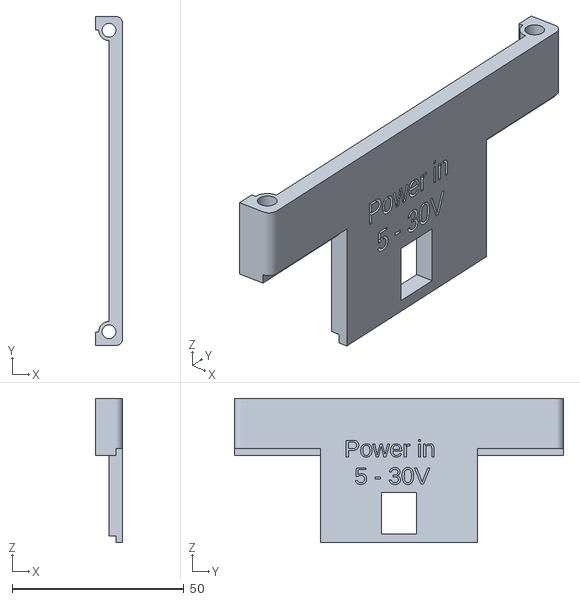
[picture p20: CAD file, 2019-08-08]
3D Designs/Stimulator/STL Files/Right.stl
8.00 x 95.8 x 42.0

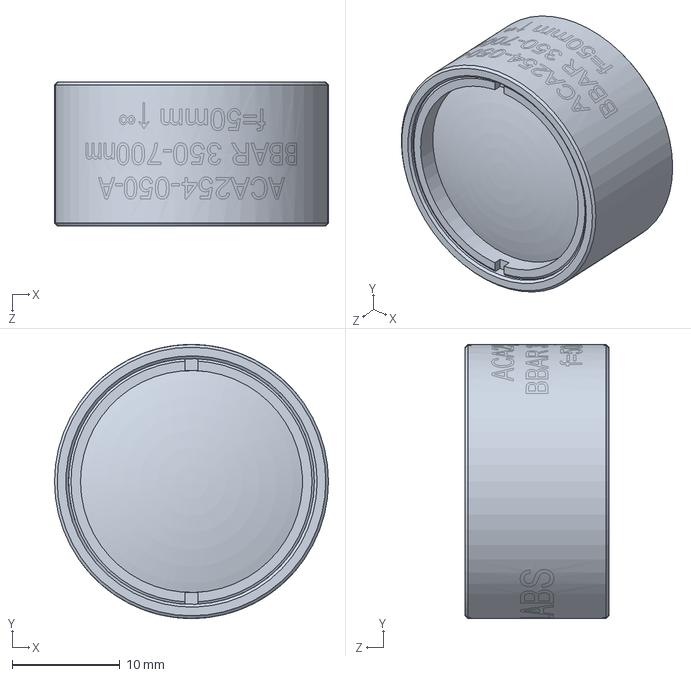
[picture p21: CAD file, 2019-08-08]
Datasheets/Optical components/Optics/50mm Achromatic Doublet lens/ACA254-050-A-Solidworks.sldprt
25.4 x 25.4 x 13.3 mm

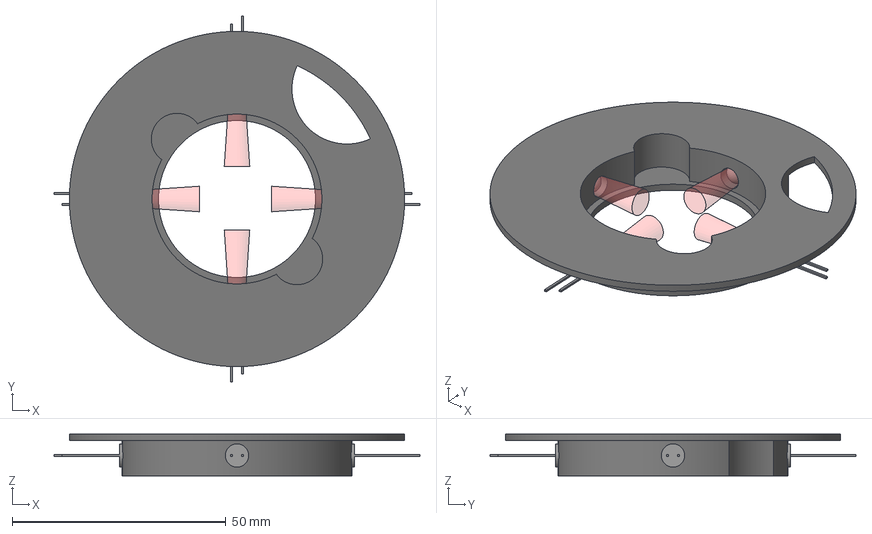
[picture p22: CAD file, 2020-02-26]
Images/FreeCAD renderings/Optogenetics - Mounting Chamber 1.FCStd
85.6 x 85.6 x 9.75 mm
LED 3mm (Red) v3
LED 3mm (Red) v004
LED 3mm (Red) v005
LED 3mm (Red) v006
OptoChamber - version1

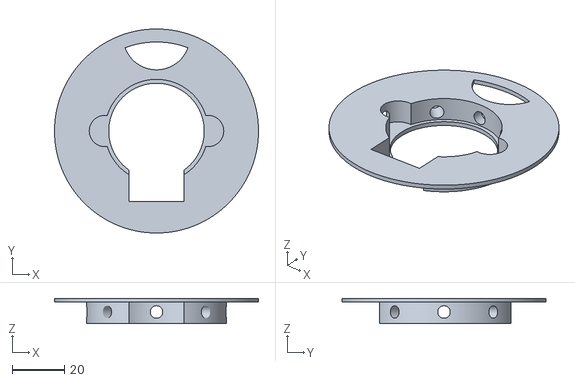
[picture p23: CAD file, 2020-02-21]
3D Designs/Optogenetics Components/STL Files/OptoChamber - Petri dish version.stl
78.4 x 78.4 x 9.75

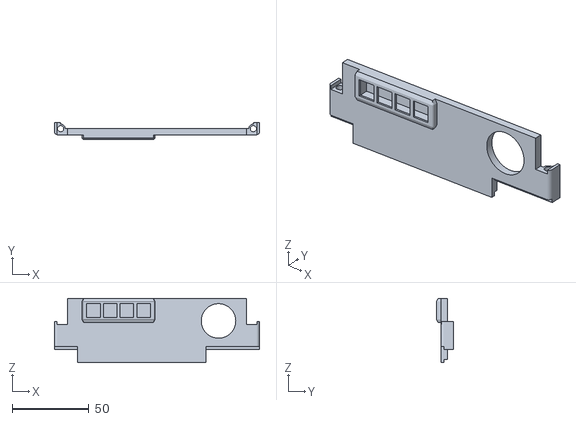
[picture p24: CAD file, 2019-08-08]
3D Designs/Stimulator/STL Files/Front.stl
133.8 x 11.0 x 42.0

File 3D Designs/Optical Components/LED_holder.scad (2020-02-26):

/* 
                 LED Holder design to fit into a Thorlab 1 inch diameter lens holder
                            
        This holder has been designed to fit into the stimulator described in:
        LED Zappelin' v2.2: An opensource LED stimulator for visual and optogenetics 
        stimulation in combination with 2-photon recording

This project is Open Source licensed, released under CERN OHL v1.2

by M.J.Y. Zimmermann, 2018.12.11
Baden Lab, CRPC, School of Life Sciences, University of Sussex, United Kingdom



// // // // // // // // // // // // // // // // // // // // // // // // // // // // //
/*                            ---  User Parameters  ---                             */

Wall = 2;           // Defines the wall thickness of the box
Smoothness = 360;   // Number of facets
tol = 0.1;          // Printing tolerance

// // // // // // // // // // // // // // // // // // // // // // // // // // // //
/*                               ---  Switches  ---                              */

n_LED = 1;          // Determine the number of LEDs to mount (from 1 to 7)


// // // // // // // // // // // // // // // // // // // // // // // // // // // //
// // // // // // // // // // // // // // // // // // // // // // // // // // // //
/*                        ---  Component Parameters  ---                        */

r_lens_1_inch    = 25.8/2;      // ThorLabs 1 inch diameter lens radius
r_inner_ring     = 22.8/2;      // ThorLabs 1 inch diameter lens ring radius
h_ring           = 2;           // ThorLabs 1 inch diameter lens ring heigh

r_LED            = 6.35/2;      // 5mm LED radius
h_LED_Holder     = 3;
d_LED_Holder     = 8;           // 5mm LED clip diameter
h_clip           = 1;           // inside 5mm LED clip heigh
r_Clip           = 7.5/2+tol;   // 5mm LED clip radius



// // // // // // // // // // // // // // // // // // // // // // // // // // // //
/*                               ---  Display  ---                               */

difference(){
    LED_holder();
    
    if (n_LED==1){
        LED_hole();
    }
    if (n_LED==2){
        for (a=[0:180:360])rotate([0,0,a])translate([0,7,0])LED_hole();
    }
    if (n_LED==3){
        for (a=[0:360/3:360])rotate([0,0,a])translate([0,d_LED_Holder,0])LED_hole();
    }
    if (n_LED==4){
        LED_hole();
        for (a=[0:360/3:360])rotate([0,0,a])translate([0,d_LED_Holder,0])LED_hole();
    }
    if (n_LED==5){
        LED_hole();
        for (a=[0:360/4:360])rotate([0,0,a])translate([0,d_LED_Holder,0])LED_hole();
    }
    if (n_LED==6){
        LED_hole();
        for (a=[0:360/5:360])rotate([0,0,a])translate([0,d_LED_Holder,0])LED_hole();
    }
    if (n_LED==7){
        LED_hole();
        for (a=[0:360/6:360])rotate([0,0,a])translate([0,d_LED_Holder,0])LED_hole();
    }
}


// // // // // // // // // // // // // // // // // // // // // // // // // // // //
/*                               ---  Modules  ---                               */

module LED_holder(){
    difference(){
        cylinder(r=r_lens_1_inch-tol, h=h_LED_Holder, $fn=Smoothness);
    
        translate([0,0,h_ring])difference(){
            cylinder(r=r_lens_1_inch, h=h_LED_Holder, $fn=Smoothness);
            cylinder(r=r_inner_ring-tol, h=h_LED_Holder, $fn=Smoothness);
        }
    } 
}

module LED_hole(){
    cylinder(r=r_LED, h=h_LED_Holder, $fn=Smoothness);
    translate([0,0,h_clip])cylinder(r=r_Clip,h=h_LED_Holder,$fn=Smoothness);
}

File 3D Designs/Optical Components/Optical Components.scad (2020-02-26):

/* 

                            Optical Component parts for
                            LED Zappelin' v2.2.
                    
        An opensource LED stimulator for visual and optogenetics stimulation in combination with 2-photon recording



This 3D file is designed to be used along ThorLabs optical cage assemblies 

Source : https://github.com/BadenLab/LED-Zappelin
This project is Open Source licensed, released under CERN OHL v1.2

by M.J.Y. Zimmermann and A.M. Chagas, 2019.02.25
Baden Lab, CRPC, School of Life Sciences, University of Sussex, United Kingdom

                                                                                     */


// // // // // // // // // // // // // // // // // // // // // // // // // // // // //
/*                            ---  User Parameters  ---                             */

Smoothness = 360;        // Number of facets. A value of 360 is recommended for a smooth print
tol = 0.1;               // Tolerance value, set by default to 0.1 for Ultimaker2 printer
Wall = 2.5;              // Wall thickness (applied only to certain modules)
wall = 2;                // Wall thickness (applied only to certain modules

// // // // // // // // // // // // // // // // // // // // // // // // // // // //
// // // // // // // // // // // // // // // // // // // // // // // // // // // //
/*                               ---  Switches  ---                              */
        LCP30 = 1;
        Mirror_Holder = 1;
        Dichroic_Frame = 1;


// // // // // // // // // // // // // // // // // // // // // // // // // // // // //
/*                         ---  Display Parameters  ---                             */

rotation = 45;      // mirror angle 
lens_offset = 1;
sep = 5;            // Separtion between objects (75 by default for proper display)


// // // // // // // // // // // // // // // // // // // // // // // // // // // //
// // // // // // // // // // // // // // // // // // // // // // // // // // // //
/*                        ---  Component Parameters  ---                        */

rod_pos2 = 60/2;         // Rod position for 60mm cage system
r_rod = 6.1/2 + tol/2;   // Rod radius 0.25 inch
S4 = 2.75/2;             // ThorLabs small holding screws 0.05 inch
r_lens_1_inch = 25.4/2;  // ThorLabs 1 inch Lens

Frame_Base = 10;
dichz = 25.4;
dichy = 1;
dichx = 36.2;

x_Frame = 36.2;
y_Frame = 3;
z_Frame = 25.4+1.5*Wall;
X_LCP30 = 73.7; //outer cube length
x_LCP30 = 40.7; //inner cube length
y_LCP30 = 40.6;
z_LCP30 = 12.70; //module thickness
y_Groove_LCP30 = 12.9;
x_arm_LCP30 = 16.5; //arm width
y_arm_LCP30 = 14; //arm length
x_ext_LCP30 = 96.3; //module diagonal length
pos_z_Screw_LCP30 = 5.6;
pos_x_screw_LCP30 = 67.3/2;
pos_y_screw_LCP30 = 26.7/2;

h_add=4;


 // // // // // // // // // // // // // // // // // // // // // // // // // // // //
/*                               ---  Display  ---                               */
if (LCP30==1){LCP();}
if (Mirror_Holder==1){translate([lens_offset,0,sep])rotate([0,0,rotation])mirror_holder();}
if (Dichroic_Frame==1){translate([lens_offset,0,z_LCP30+h_add+Frame_Base+2*sep])rotate([0,0,rotation])dich_frame();}


// // // // // // // // // // // // // // // // // // // // // // // // // // // //
/*                               ---  Modules  ---                               */

module LCP(){
difference(){
        union(){
            translate([-X_LCP30/2,-y_LCP30/2,0])cube([X_LCP30,y_LCP30,z_LCP30]);
             minkowski(){
                translate([-x_LCP30/2+2*tol+Wall,-y_LCP30/2+Wall,z_LCP30])cube([x_LCP30-2*tol-2*Wall,y_LCP30-2*Wall,h_add-Wall]);
                cylinder(r1=Wall,h=Wall,$fn=Smoothness);
            }
        }
        
        difference(){
           translate([-X_LCP30/2,-y_Groove_LCP30/2,0])cube([X_LCP30,y_Groove_LCP30,z_LCP30]);
           translate([-x_LCP30/2,-y_LCP30/2,0])cube([x_LCP30,y_LCP30,z_LCP30]);
        }
        
        Screw_LCP30();
        translate([lens_offset,0,0])cylinder(r=r_lens_1_inch,h=z_LCP30+h_add,$fn=Smoothness);
        
        //customisation
        translate([-X_LCP30/2,-y_LCP30/2,0])cube([X_LCP30/2-x_LCP30/2+2*tol,y_LCP30,z_LCP30]);
    }
    //customization
    difference(){
        
        translate([-X_LCP30/2,-y_Groove_LCP30/2+2*tol,0])cube([X_LCP30/2-x_LCP30/2+2*tol,y_Groove_LCP30-4*tol,z_LCP30]);
        
        Screw_LCP30();
        translate([-pos_x_screw_LCP30,0,0])cylinder(r=S4,h=z_LCP30,$fn=Smoothness);
    }
}

module Screw_LCP30(){ 
    translate([pos_x_screw_LCP30,pos_y_screw_LCP30,0])cylinder(r=S4,h=z_LCP30,$fn=Smoothness);
    translate([pos_x_screw_LCP30,-pos_y_screw_LCP30,0])cylinder(r=S4,h=z_LCP30,$fn=Smoothness);
    
    translate([rod_pos2,-y_LCP30/2,pos_z_Screw_LCP30])rotate([-90,0,0])cylinder(r=r_rod,h=y_LCP30,$fn=Smoothness);
    translate([-rod_pos2,-y_LCP30/2,pos_z_Screw_LCP30])rotate([-90,0,0])cylinder(r=r_rod,h=y_LCP30,$fn=Smoothness);
    
    
    translate([x_LCP30/2,0,z_LCP30+h_add/3])rotate([0,-90,0])cylinder(r=S4,h=x_LCP30/2,$fn=Smoothness);
    translate([x_LCP30/2,0,h_add+3])rotate([0,-90,0])cylinder(r=S4,h=x_LCP30/2,$fn=Smoothness);
    translate([0,x_LCP30/2,z_LCP30+h_add/3])rotate([90,0,0])cylinder(r=S4,h=x_LCP30/2,$fn=Smoothness);
    translate([0,-x_LCP30/2,z_LCP30+h_add/3])rotate([-90,0,0])cylinder(r=S4,h=x_LCP30/2,$fn=Smoothness);
}

module mirror_holder(){
cylinder(r=r_lens_1_inch-tol,h=z_LCP30+Wall+h_add,$fn=Smoothness);
    
translate([0,0,z_LCP30+h_add])difference(){
    translate([-x_Frame/2-1.5*Wall,-y_Frame/2-Wall,0])cube([x_Frame+3*Wall,y_Frame+2*Wall,z_Frame+Frame_Base]);
    
    translate([-x_Frame/2-tol,-y_Frame/2-Wall,Frame_Base])cube([x_Frame+2*tol,y_Frame+2*Wall,z_Frame+tol]);
    translate([-x_Frame/2-Wall-tol,-y_Frame/2-wall/2-tol,Frame_Base-Wall/2])cube([x_Frame+2*Wall+2*tol,y_Frame+wall+2*tol,z_Frame+Wall/2+tol]);
}
}

module dich_frame(){
difference(){    
    translate([-x_Frame/2-Wall,-y_Frame/2-wall/2,0])cube([x_Frame+2*Wall,y_Frame+wall,z_Frame]);

    translate([-dichx/2-tol,-y_Frame/2-wall/2,Wall-tol])cube([dichx+2*tol,dichy+wall/2,dichz+2*tol]);
    translate([-dichx/2+wall/2,-y_Frame/2-Wall,Wall-tol+wall/2])cube([dichx-wall,y_Frame+2*wall,dichz-wall]);
    translate([-Wall,-y_Frame/2-wall/2,z_Frame-Wall])cube([2*wall,dichy+wall/2,Wall]);
}
}

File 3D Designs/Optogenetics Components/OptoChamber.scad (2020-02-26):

/* 

                            Opto Chamber v1.1
                            
    
 
This 3D file is designed for the Multi-Chromatic Stimulator project components and its customed PCB
Source : https://github.com/BadenLab/LED-Zappelin
This project is Open Source licensed, released under CERN OHL v1.2

by Tom Baden
modified by MJY Zimmermann
Baden Lab, CRPC, School of Life Sciences, University of Sussex, United Kingdom, www.badenlab.org 

and Sinziana Pop
Prieto Lab, Francis Crick Institute, United Kingdom
                                                                                     */


// // // // // // // // // // // // // // // // // // // // // // // // // // // // //
/*                            ---  User Parameters  ---                             */

tol = 0.1;                // Printing tolerance
wall = 1.5;               // Defines the wall thickness of the chamber
Smoothness = 30;         // Number of facets


// // // // // // // // // // // // // // // // // // // // // // // // // // // //
// // // // // // // // // // // // // // // // // // // // // // // // // // // //
/*                               ---  Switches  ---                              */

Version = 2;              // Select either version 1 or 2, or enter 0 for no display
Platform = 1;             // Enter 1 for displaying the mounting platform, 0 to hide it


// // // // // // // // // // // // // // // // // // // // // // // // // // // //
// // // // // // // // // // // // // // // // // // // // // // // // // // // //
/*                        ---  Component Parameters  ---                        */

thickwall = 7;            // Inner circle thickness
Asub_r = 39.5/2 + tol;    // Petri dish hole radius 
R_Accessgroove = 6;       // Access groove radius

A_h= wall;                // Chamber heigh
A_r = 39.2;               // Chamber radius
A_h2= 9;                  // Inner circle heigh
A_r2= Asub_r + thickwall; // Inner circle radius

A_LED_r = 2.3 + tol;      // LED holder radius
A_LED_zpos = A_h2-4.5;    // LED holder heigh position

Olf_width = 21;           // Width for the olfactory system

mount_width = 50.8;       // Platform width
stage_depth = 8;          // Stage height
stage_width = 100;        // Stage width
stage_length = 75;        // Stage length


rect_hole_width = 23;
rect_hole_length = 100;
rect_hole_y = 70;

circ_hole_rad = 32.5+tol;

screw_rad = 6/2+tol;
screw_coord1 = 12.9;
screw_coord2 = 37.9;


magnet_rad = 14/2+tol;    // Mounting magnet radius
magnet_depth = 3+tol;     // Mounting magnet height

magnet1_x = -15;          // First magnet x_position
magnet1_y = 116;          // First magnet y_position

magnet2_x = 66;           // Second magnet x_position
magnet2_y = 61;           // Second magnet y_position



 // // // // // // // // // // // // // // // // // // // // // // // // // // // //
/*                               ---  Display  ---                               */

if (Version==1){rotate([0,0,40])
    difference(){ 
        A();
        Asub(); 
    }
    difference(){ 
        B();
        Bsub(); 
    }
}
 
if (Version==2){rotate([0,0,45])
    difference(){ 
        A2();
        A2sub(); 
    }   
    difference(){ 
        B2();
        B2sub(); 
    }
}

if (Platform==1){
    translate([-25,-90,-9])stage();
}


// // // // // // // // // // // // // // // // // // // // // // // // // // // //
/*                               ---  Modules  ---                               */

module A() {
	translate([0,0,0])rotate([0,0,0])cylinder($fn=Smoothness, r=A_r, h=A_h, center=true); // Main_rim
	translate([0,0,-A_h2/2])rotate([0,0,0])cylinder($fn=Smoothness, r=A_r2, h=A_h2, center=true); // Main_sub
}

module Asub() {
	translate([0,0,-A_h2/2+wall])rotate([0,0,0]){cylinder($fn=Smoothness, r=Asub_r, h = A_h2, center = true); } // Main	
    translate([0,0,-A_h2/2+wall]){ rotate([0,0,0]){ cylinder( $fn=Smoothness, r = Asub_r-wall, h = 100, center = true); }} // Through hole

    translate([Asub_r*sqrt(2)/2,-Asub_r*sqrt(2)/2,-A_h2/2+wall]){ rotate([0,0,0]){ cylinder( $fn=Smoothness, r = R_Accessgroove, h = A_h2, center = true); }} // Chamber access-aid hole	

    translate([-Asub_r*sqrt(2)/2,Asub_r*sqrt(2)/2,-A_h2/2+wall]){ rotate([0,0,0]){ cylinder( $fn=Smoothness, r = R_Accessgroove, h = A_h2, center = true); }} // Chamber access-aid hole	

    translate([sqrt(2)*A_r/2-2,sqrt(2)*A_r/2-2,-A_h2/2+wall]){ rotate([0,0,0]){ cylinder( $fn=Smoothness, r = Asub_r-thickwall, h = 100, center = true); }} // Cable hole

	translate([0,0,-A_LED_zpos]){ rotate([0,90,0]){ cylinder( $fn=Smoothness, r = A_LED_r, h = 100, center = true); }} // LEDs
	translate([0,0,-A_LED_zpos]){ rotate([90,0,0]){ cylinder( $fn=Smoothness, r = A_LED_r, h = 100, center = true); }} // LEDs
}

module B() {
	translate([0,0,0]){ rotate([0,0,0]){ cylinder( $fn=Smoothness, r = A_r, h = A_h, center = true); }} // Main_rim
}


module Bsub() {
	translate([0,0,-A_h2/2+wall]){ rotate([0,0,0]){ cylinder( $fn=Smoothness, r = A_r - 5, h = A_h2, center = true); }} // Main	
}

module A2() {
	translate([0,0,0]){ rotate([0,0,0]){ cylinder( $fn=Smoothness, r = A_r, h = A_h, center = true); }} // Main_rim
	translate([0,0,-A_h2/2]){ rotate([0,0,0]){ cylinder( $fn=Smoothness, r = A_r2, h = A_h2, center = true); }} // Main_sub
}

module A2sub() {
	translate([0,0,-A_h2/2+wall]){ rotate([0,0,0]){ cylinder( $fn=Smoothness, r = Asub_r, h = A_h2, center = true); }} // Main	
    translate([0,0,-A_h2/2+wall]){ rotate([0,0,0]){ cylinder( $fn=Smoothness, r = Asub_r-wall, h = 100, center = true); }} // Through hole

    translate([Asub_r*sqrt(2)/2,-Asub_r*sqrt(2)/2,-A_h2/2+wall]){ rotate([0,0,0]){ cylinder( $fn=Smoothness, r = R_Accessgroove, h = A_h2, center = true); }} // Chamber access-aid hole	

    translate([-Asub_r*sqrt(2)/2,Asub_r*sqrt(2)/2,-A_h2/2+wall]){ rotate([0,0,0]){ cylinder( $fn=Smoothness, r = R_Accessgroove, h = A_h2, center = true); }} // Chamber access-aid hole	

    translate([sqrt(2)*A_r/2-2,sqrt(2)*A_r/2-2,-A_h2/2+wall]){ rotate([0,0,0]){ cylinder( $fn=Smoothness, r = Asub_r-thickwall, h = 100, center = true); }} // Cable hole

	translate([0,0,-A_LED_zpos]){ rotate([0,90,0]){ cylinder( $fn=Smoothness, r = A_LED_r, h = 100, center = true); }} // LEDs
	translate([0,0,-A_LED_zpos]){ rotate([90,0,0]){ cylinder( $fn=Smoothness, r = A_LED_r, h = 100, center = true); }} // LEDs

    translate([0,0,-A_LED_zpos]){ rotate([45,90,0]){ cylinder( $fn=Smoothness, r = A_LED_r, h = 100, center = true); }} // LEDs NEW
	translate([0,0,-A_LED_zpos]){ rotate([-45,90,0]){ cylinder( $fn=Smoothness, r = A_LED_r, h = 100, center = true); }} // LEDs NEW

    translate([-Asub_r+5,-Asub_r+5,0]){ rotate([0,0,45]){ cube([12,Olf_width,100], center = true); }} // Olfaction stuff hole	
}

module B2() {
	translate([0,0,0]){ rotate([0,0,0]){ cylinder( $fn=Smoothness, r = A_r, h = A_h, center = true); }} // Main_rim  
}

module B2sub() {
	translate([0,0,-A_h2/2+wall]){ rotate([0,0,0]){ cylinder( $fn=Smoothness, r = A_r - 5, h = A_h2, center = true); }} // Main
}

module stage() {
    difference() {
        stage_add();
        stage_sub();
    }
}


module stage_add() {
    cube([mount_width,mount_width,stage_depth]);
    translate([-(stage_width - mount_width)/2,mount_width,0]) {
        cube([stage_width,stage_length,stage_depth]);
    };
    
}

module stage_sub() {
    
    // round stage hole
     translate([mount_width/2,mount_width + stage_length - circ_hole_rad,0]) {
        cylinder(stage_depth,circ_hole_rad,circ_hole_rad, $fn=Smoothness);
    };
    
    // space for olfactory stimulator
    translate([(mount_width - rect_hole_width)/2,rect_hole_y,0]) {
        cube([rect_hole_width,rect_hole_length,stage_depth]);
    };
    
     // center M6 screw hole
    translate([mount_width/2,mount_width/2,0]) {
        cylinder(stage_depth,screw_rad,screw_rad, $fn=Smoothness);
    };
    
     // top left M6 screw hole
    translate([screw_coord1,screw_coord2,0]) {
        cylinder(stage_depth,screw_rad,screw_rad, $fn=Smoothness);
    };
    
     // top right M6 screw hole
    translate([screw_coord2,screw_coord2,0]) {
        cylinder(stage_depth,screw_rad,screw_rad, $fn=Smoothness);
    };
    
     // bottom left M6 screw hole
    translate([screw_coord1,screw_coord1,0]) {
        cylinder(stage_depth,screw_rad,screw_rad, $fn=Smoothness);
    };
    
     // bottom right M6 screw hole
    translate([screw_coord2,screw_coord1,0]) {
        cylinder(stage_depth,screw_rad,screw_rad, $fn=Smoothness);
    };
    
 
     // magnet hole 1
    translate([magnet1_x,magnet1_y,stage_depth - magnet_depth]) {
        cylinder(magnet_depth,magnet_rad,magnet_rad, $fn=Smoothness);
    };
    
    
      // magnet hole 2
    translate([magnet2_x,magnet2_y,stage_depth - magnet_depth]) {
        cylinder(magnet_depth,magnet_rad,magnet_rad, $fn=Smoothness);
    };
    
}

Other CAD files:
3D Designs/Optical Components/STL Files/7_LED_Holder.stl
Datasheets/Optical components/Optics/50mm Achromatic Doublet lens/ACA254-050-A-Step.step
3D Designs/Stimulator/LED Zappelin' v2.2.scad
3D Designs/Optical Components/STL Files/2_LED_Holder.stl
3D Designs/Optical Components/STL Files/3_LED_Holder.stl
3D Designs/Optical Components/STL Files/4_LED_Holder.stl
3D Designs/Optical Components/STL Files/5_LED_Holder.stl
3D Designs/Optical Components/STL Files/LCP30 - modified.stl
3D Designs/Optical Components/STL Files/dichroic_frame.stl
3D Designs/Optical Components/STL Files/dichroic_holder.stl
3D Designs/Stimulator/MultiChromatic Stimulator v2.1.scad
3D Designs/Stimulator/STL Files/Bottom.stl
3D Designs/Stimulator/STL Files/Left.stl
Images/FreeCAD renderings/Optogenetics - Experimental setup.FCStd

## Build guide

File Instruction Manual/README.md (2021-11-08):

<p align="right">
<h1 align="center">Instruction Manual</h1></p>

***

## Overview

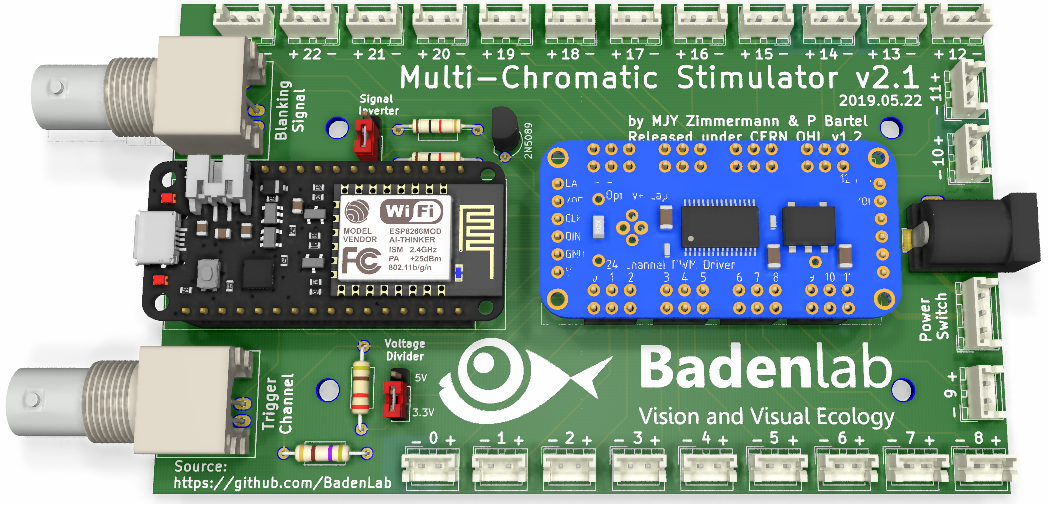
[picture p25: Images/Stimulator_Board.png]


<p align="justify">This document contains detailed assembly instructions, a software guideline to customize stimuli, and includes a parts list.</p>

 The Arduino code and 3D printing files (SCAD and STL) can be downloaded [here](https://github.com/BadenLab/LED-Zappelin/tree/master/3D%20Designs), and further modified to fit customise purposes. The aim of this device is to finely control LEDs used in combination with a 2-photon microscope.

The device consists of a custom-designed PCB, an [ESP32 development board](https://learn.adafruit.com/adafruit-huzzah32-esp32-feather) (or an Arduino Nano if the stimulator does not need to be combined with a 2 photon microscope), a [LED driver](https://learn.adafruit.com/tlc5947-tlc59711-pwm-led-driver-breakout/overview) and various off-the-shelf components.

***

- [Assembling the Stimulator](#Assembling-the-Stimulator)
- [Programming the Stimulator](#Programming-the-ESP32)
- [Operating the Stimulator](#Operating-the-Stimulator)
- [Calibrating the Stimulator](#Calibrating-the-Stimulator)

***

## Assembling the stimulator

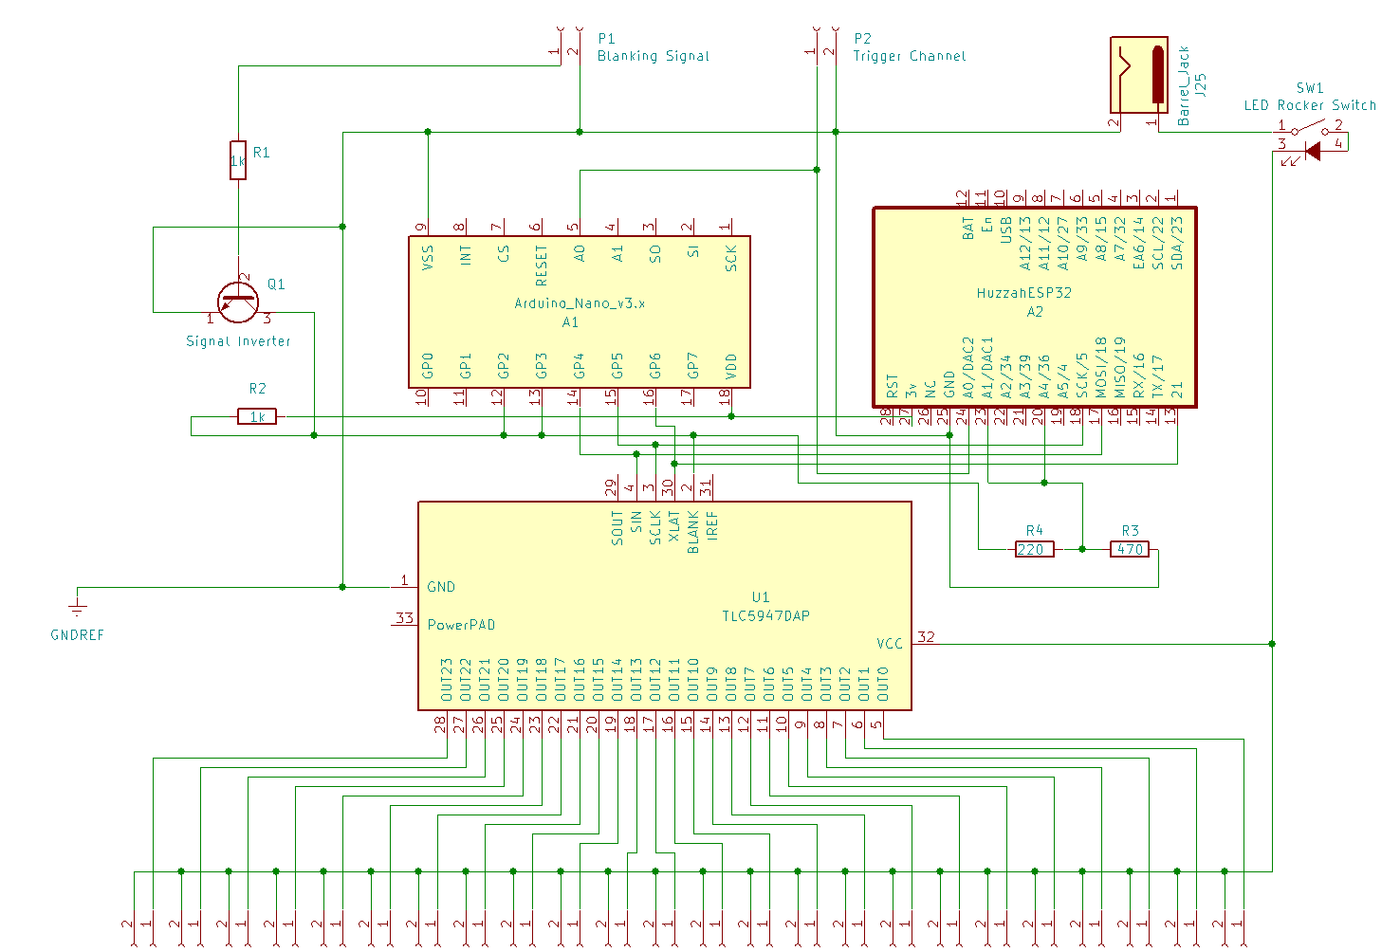
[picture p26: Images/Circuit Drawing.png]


<p align="center"><h4 align="left">1 – Obtaining the custom-designed PCB</h4></p>

From the GitHub repository, one can find the [gerber.zip folder](https://github.com/BadenLab/LED-Zappelin/tree/master/PCB/Stimulator) needed to order the PCB to any manufacturer company (i.e. https://jlcpcb.com).

Ordering a minimum of five units should not cost more than £10. Gerber files were designed with [KiCad 5.0](http://kicad.org/).

Schematics and PCB footprint can be downloaded and modified from the same repository if need be.

****

<p align="center"><h4 align="left">2 – Soldering the custom-designed PCB</h4></p>
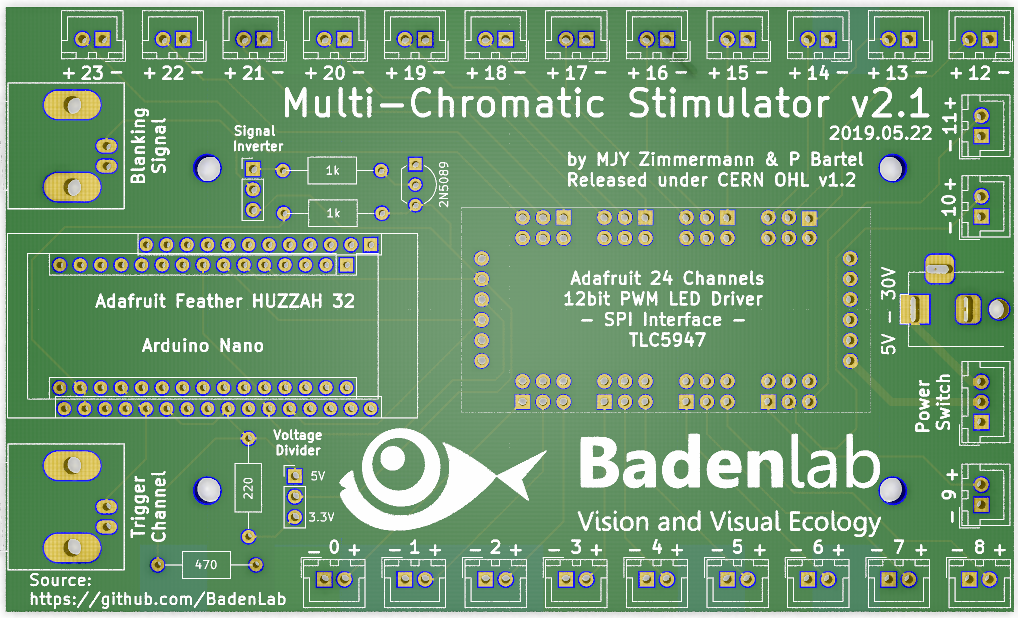
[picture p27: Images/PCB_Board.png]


<p align="justify">The board is self-explanatory. On the left, two options are available, one for the Arduino (close rows) the other for the ESP (spread rows). There is no need to solder more JST pins that the number of LED required for the desired stimulator.

<p align="justify">The jumper on the top (Signal Inverter) allows the inversion of the TTL "Blanking" signals. For ScanImage users, the jumper should be placed at the upper position.

<p align="justify">The jumper at the bottom of the board (Voltage Divider) allows to tune down the voltage from 5 to 3.3V if the ESP is used instead of an Arduino. ESP32 unlike Arduino Nano, works on a 3.3V logic; no higher tension should be sent to this board. Since most TTL deliver 5V pulses, we selected a 220/470Ω divider to bring a 5V blanking signal into a 3.3V input. Depending on the blanking signal generator used, this divider can be modified to fit one’s personal design or bypassed by only bridging the 220Ω resistor.

</br>
</br>

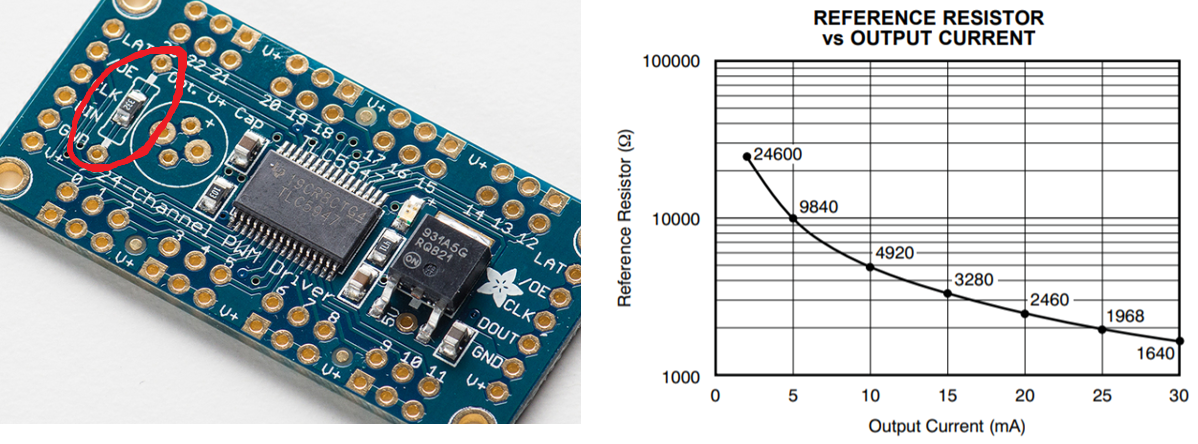
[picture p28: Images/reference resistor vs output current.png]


<p align="justify">The Adafruit TLC5947 LED driver is a constant current driver configured by default to set the current level at 15mA per channel, which is virtually safe for any LED. However, one can operate at different current by replacing the on-board reference resistor with a through hole resistor. The driver is capable to deliver up to 30mA, the graph below shows the relationship between resistance and output current. </p>

****

<p align="center"><h4 align="left">3 – Mounting the potentiometer</h4></p>
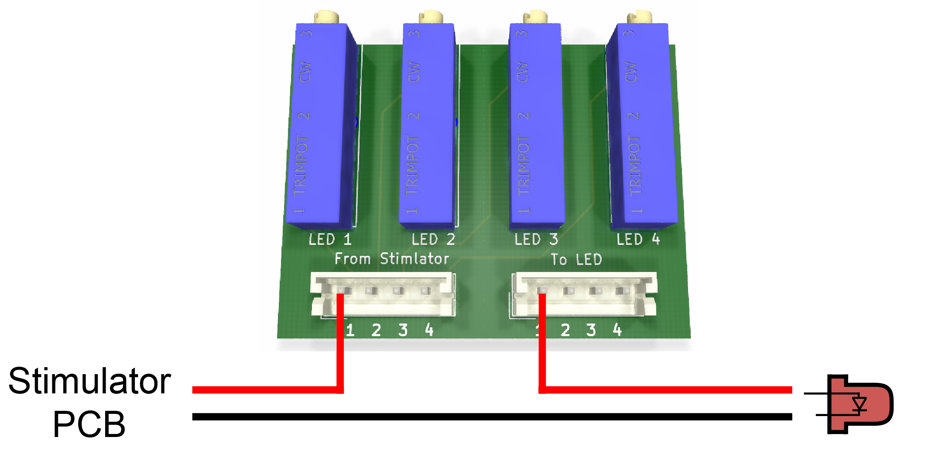
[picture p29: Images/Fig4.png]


In order to finely adjust each LED power, we added multiple-turn trimmer potentiometers to our design. A simple solution is to manufacture the appropriate PCB board (We provide multiple options on the [GitHub repository](https://github.com/BadenLab/LED-Zappelin/tree/master/PCB/Potentiometer%20Mounts)).

<p align="justify">Otherwise, one can make its own little PCB by using a solderable board.
Each potentiometer connects its ClockWise (pin 3) to the LED (+) stimulator JST pin; and its Base (pin 2) to the LED (+) leg. The LED (-) stimulator JST pin connects the LED (-) leg directly.</p>

***

<p align="center"><h4 align="left">4 – Printing the Stimulator box</h4></p>

[STL files](https://github.com/BadenLab/LED-Zappelin/tree/master/3D%20Designs/Stimulator/STL%20Files) can be found on the GitHub repository and print directly if the user wishes to go for the default design (4 stimulation LEDs + 4 proxy LEDs) and [BoM](https://github.com/BadenLab/LED-Zappelin/blob/master/Bills%20of%20Materials/BOM%20-%20Stimulator.ods).

However, [SCAD files](https://github.com/BadenLab/LED-Zappelin/blob/master/3D%20Designs/Stimulator/MultiChromatic%20Stimulator%20v2.1.scad) are also available and easily adjustable for personalised design.

We used [OpenSCAD](www.openscad.com) to design the stimulator box. The tolerance of the printer can be adjusted in the “USER Parameters” section of the script (tol =0.1; by default, this value is used for Prusa MK3 and Ultimaker 2). Each component can be displayed/design individually in the “Switches” section. Variables such as LED number (4 by default) and the potentiometer board dimensions can be adjusted in the “Component Parameters” section.

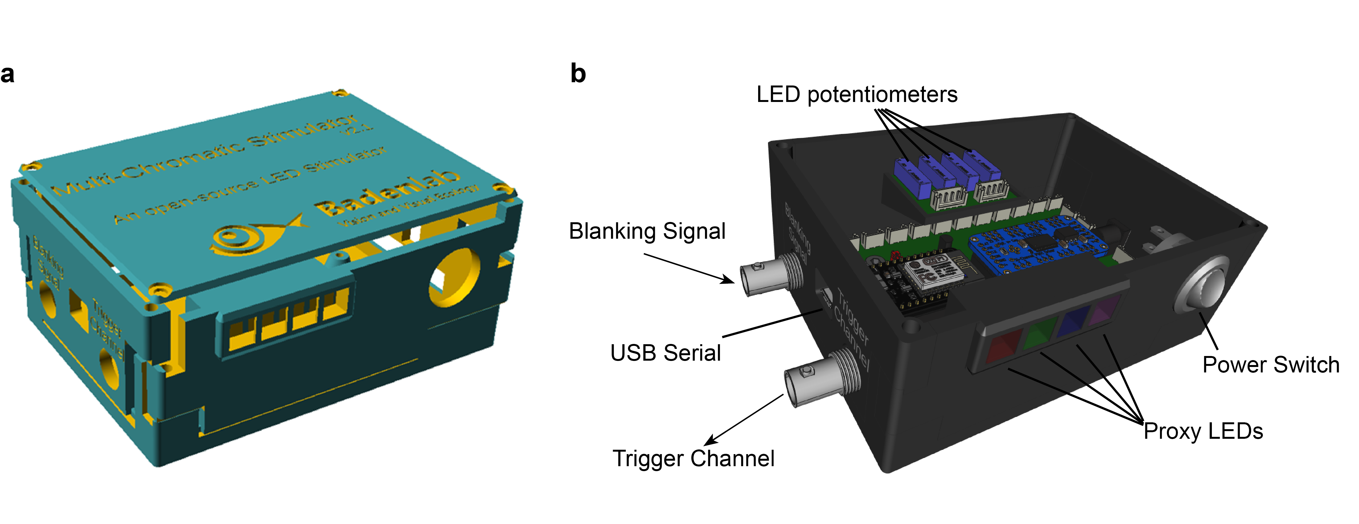
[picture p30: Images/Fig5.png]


<h5 align="justify">a) Rendering of the stimulator box 3D files set here by default for 4 LED channels and 4 proxy LEDs. b) Rendering of the fully mounted stimulator with all PCBs and components tightly fitting their respective space. </h5>

<p align="justify">The PCB is screwed to the “Bottom” part of the box by using M3 screws and nuts. The potentiometer board adjusts itself with the “Back” part of the box, and the trimmers should adapt to their respective holes exactly.
All part should fit tightly together and are maintained together by 4 M3*50mm socket screws. </p>

***

<p align="center"><h4 align="left">5 – Adjusting the proxy LED</h4></p>
<p align="justify">The proxy LED are markers for the experimenter to have a ready visualisation of the stimulus being displayed under the objective. If this option is selected, 3mm LEDs are to be mounted at the back of the LED holder using 3mm LED mounts.

<p align="justify">Finally, any translucid material could be placed in the LED holder slot in order to diffuse the proxy LED light (In our example, we used a piece of thin Teflon)</p>

***

<p align="center"><h4 align="left">6 – Mounting the stimulating LEDs</h4></p>
<p align="justify">Each stimulating LED must be connected to its respective channel, taking note of their polarity (long LED leg should be connected to the positive pin).

<p align="justify">For our visual stimulation setup, we combined all LED light sources into one beam which is projected through the objective to our model retina. We therefore constructed an optical cage system using a mixture of Thorlabs parts and 3D-printed objects to hold all filters and dichroic mirrors.

<p align="justify">For the optogenetics experiment we 3D-designed arenas where the sample sits, surrounded by  four LEDs. </p>

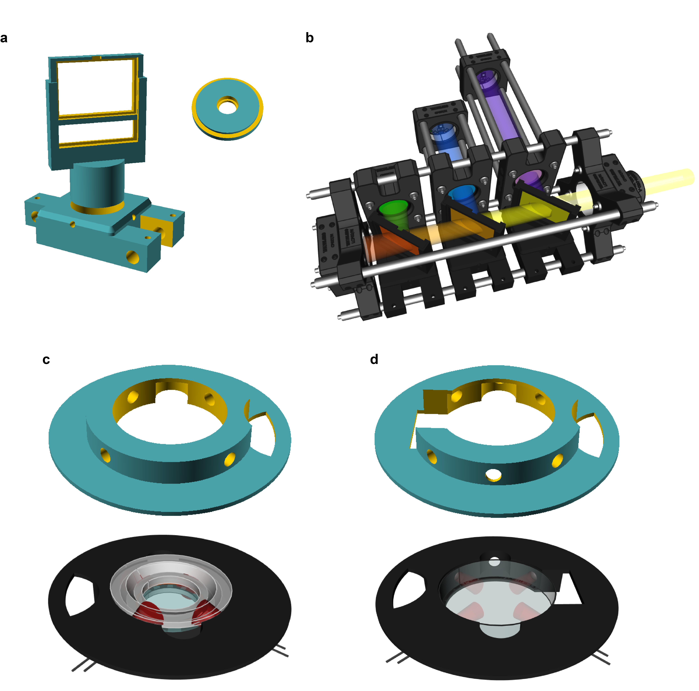
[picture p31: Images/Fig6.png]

<h5 align="justify">a) SCAD files for adapting 3mm LEDs and dichroic mirrors to standard 30mm optomechanical system. b) Rendering of the LED illumination system for the visual experiment. c) For optogenetics experiment, we designed a mounting platform that holds four 3mm LEDs and can fit a RC-40HP chamber (SmartEphys, Warner Instrument).  d) Same as c) but designed to fit a small petri dish (ø 35mm) lid. </h5>

***

<p align="center"><h4 align="left">7 – Connecting the stimulator to LEDs, the microscope’s DAQ and a computer</h4></p>
<p align="justify">The stimulator can be externally powered anywhere between 5-30V via the power port. Since the TLC5947 is constant current LED driver, the voltage selection is not critical, however it should be slightly higher than the LED forward voltage (cf. LED driver datasheet). If desired, multiple LEDs can be connected to the same channel, however in this case the voltage supply must be adjusted accordingly (cf. LED driver datasheet).

<p align="justify">For the standard line-synched stimulator version with an ESP32, a line-synched 5V TTL blanking signal BNC must be fed into the stimulator from the microscope’s DAQ (if the TTL is different from 5V, this can still be accepted provided the associated resistor is changed accordingly – see soldering paragraph). Note: Since for the default ESP32 version the blanking signal is used as the external clock, the stimulator will not execute any stimuli without it. If such line-synching is not required, consult the “simple” non-synchronised version using the Arduino Nano.

<p align="justify">If required, connect the output trigger channel to the microscope’s DAQ. This signal generated by the stimulator by default sends a 3.3V pulse (if ESP32 is used, 5V for Arduino Nano) once at the start of the stimulus and then again every 1,000 ms (1 Hz exactly). The trigger signal can for example be used to time-align acquired imaging data with the stimulus in postprocessing.

<p align="justify">Finally, the board is connected to a computer via USB (micro USB for ESP32, mini USB for Arduino Nano). </p>

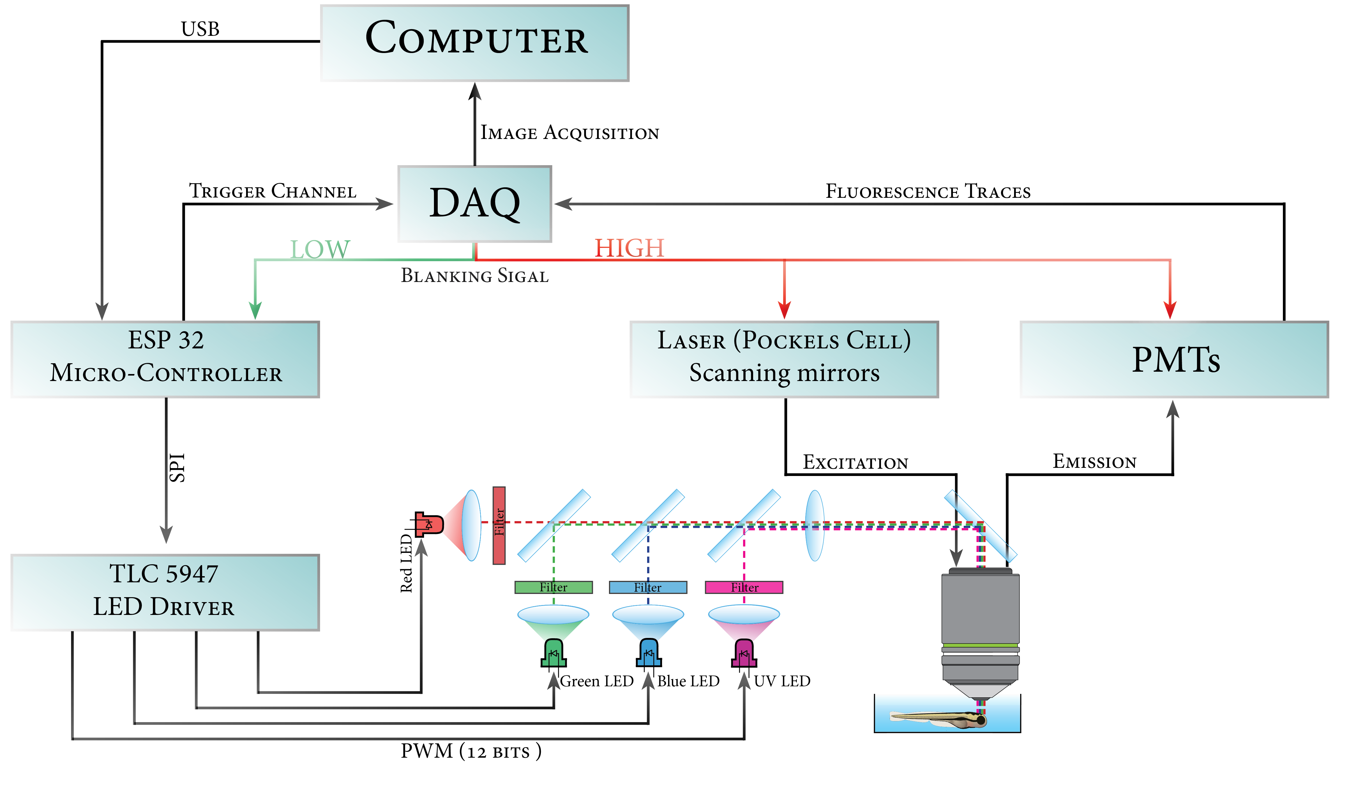
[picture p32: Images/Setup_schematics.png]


***

## Programming the ESP32

1-	Download and install [Arduino environment](www.arduino.org) on the computer.

2-	To use the ESP32, a couple of steps are necessary
Install the latest SiLabs [CP2104 driver](https://www.silabs.com/products/development-tools/software/usb-to-uart-bridge-vcp-drivers).
Follow the installation instructions from the [Espressif repository](https://github.com/espressif/arduino-esp32/blob/master/docs/arduino-ide/boards_manager.md).

3-	Install the TLC5947 library:	Start Arduino and from the “Sketch” tab, select “Include Library” and open “ Manage Libraries”.	From the search bar enter “TLC5947”. Select and Install the library

4-	Close Arduino and open the Multi-Chromatic-Stimulator arduino file from the [Arduino Code folder](https://github.com/BadenLab/LED-Zappelin/tree/master/Arduino%20code/2-Photon_Mutli_Chromatic_Stimulator).

<p align="justify">5-	From the “Tools” tab: Select from “Boards” the “Adafruit ESP32 Feather”.	From “Upload Speed”, select 921600.	From “Flash Frequency”, select 80Hz. From “Port”, select the computer port to which the ESP is connected (if doubt, unplug, replug and observe the choices differences). If the ESP is not recognised, check the driver installation (2), then check the micro USB cable. </p>

6-	Compile and Upload the code by clicking on the arrow button on the top left.

7-	The stimulator is ready to be used.

***

## Operating the Stimulator
<p align="center"><h4 align="left">The code is organised in five distinct part:</h4></p>

  <h4>Stimulus Parameters</h4>

<p align="justify">The code is designed to iteratively loop a pre-programmed stimulus sequence after an initial one-off optional preadaptation period

<p align="justify">- The number of loops is determined by *nLoops*. The stimulus will stop after finishing the nth  loop.

<p align="justify">–	IMPORTANT,  the number of entries within the arrays must be the same and manually entered in *nArrayEntries* (including the pre-adaptation at position 1, see below).

<p align="justify">–	The *Scan_Logic* parameter corresponds to the x-mirror scan rate in ms (i.e. = 1.0 if line speed is 1 ms per line). This value must be changed if a different scan logic is used. This value defines the tempo of the entire stimulus (Each time a blanking signal is counted, the code advances by an internal time-counter of Scan_Logic in milliseconds.)

<p align="justify">–	The *array_LED#* arrays correspond to the stimulus sequence for each LED number. Here the number of arrays must be adjusted to the number of stimulating LEDs. All array positions will be read in synchrony, based on the timing array detailed below. IMPORTANT: The first entry is not part of the to-be-looped stimulus sequence, but instead defines the LED’s brightness for the preadaptation period. Note also that the first trigger output will start with the second entry (= the first entry of the stimulation sequence). The value entered at each position is the light intensity where 0 corresponds to no light and 100 to maximal light intensity. The value entered must range between 0 and 100.

<p align="justify">–	The *array_Time* array corresponds to the duration of each entry in ms; the first entry being the pre-adaptation that will only be played at the start of the stimulus, the sequence will then loop starting at the second position. </p>

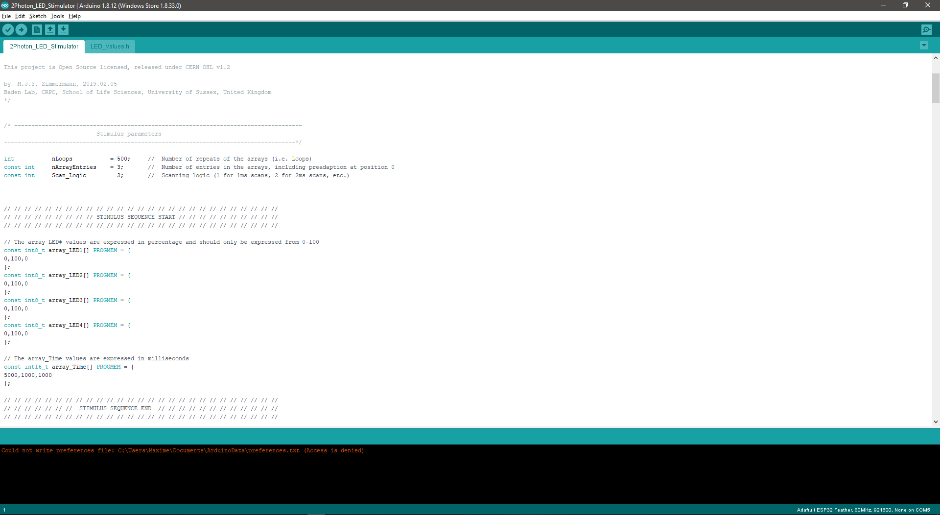
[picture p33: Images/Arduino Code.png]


For example, if …

nLoops = 3;

nArrayEntries = 3;

Scan_Logic = 1.0;

Array_LED1 = {50,100,0};

Array_LED2 = {50,0,100};

Array_Time = {5000,1000,1000};

… the resultant stimulus will start with 5 seconds of both LEDs being set to 50% intensity (preadaptation) and will thereafter switch back and forth every 1 second between 100% and 0% power for the two LEDs in antiphase, for 3 repetitions.

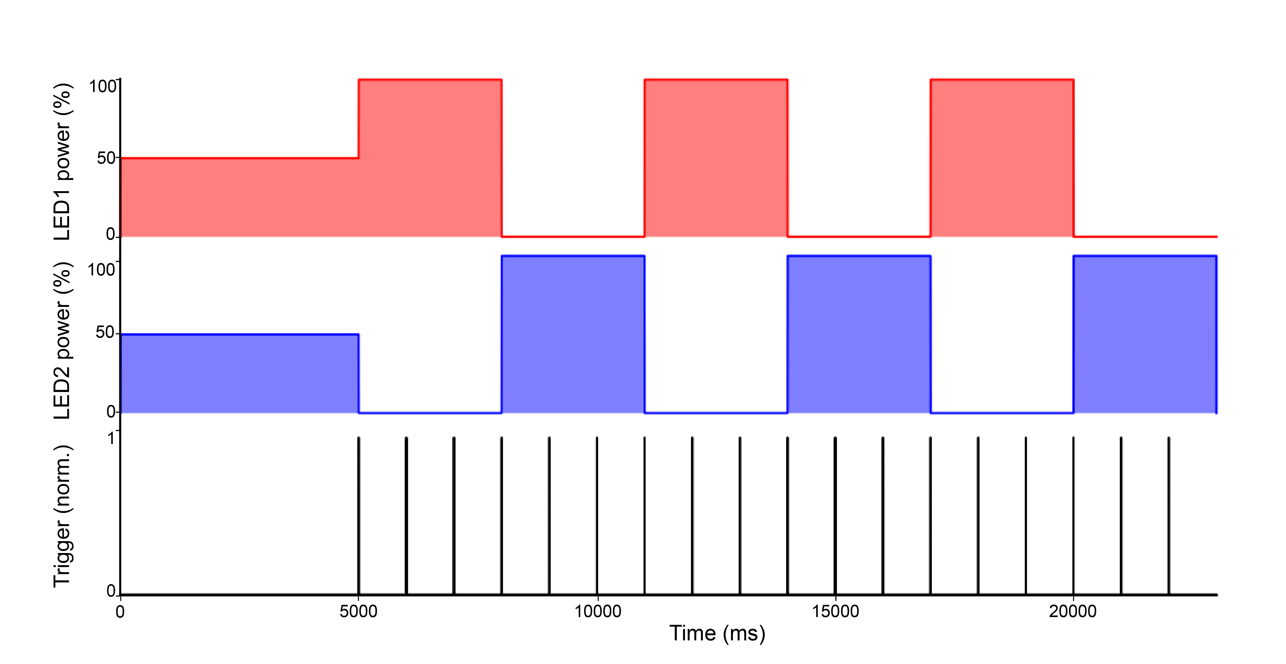
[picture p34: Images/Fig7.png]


***

  <h4>Microcontroller Board Selection</h4>

This is where the user defines if he is using an ESP32 or an Arduino Nano

***

  <h4>Internal Definitions</h4>

This is the main definition part of the code which can be modified to:

-	Add more LEDs than the 4 main and 4 proxy defined by default. (Global variables, the LED pins correspond to the pin number on the TLC5947).

-	Adjust the Trigger duration (25 ms by default). This value corresponds to the amount of time the trigger marker will remain on in order to be detected by i.e. a DAQ.

-	Adjust the Trigger interval (1000 ms by default). Value between two successive triggers.

***

  <h4>Internal Methods</h4>

This is the main core of the code and should not be structurally changed (apart from adding more LEDs, as required).

***

  <h4>Main Loop</h4>

This is where the stimuli controls are defined. By default, when compile window is open (magnifying glass on the top right corner) and the baud rate at the bottom right of the window has be changed to 115200, a manual command will trigger a stimulus:

By default:

This is where the serial user controls are defined. By default, when the serial monitor is open (magnifying glass on the top right corner in the Arduino IDE) and the baud rate at the bottom right of the window has be changed to 115,200, a manual command followed by pressing “enter” will trigger a stimulus:
      By default:

-	When *a* is entered in the serial monitor, the stimulator will play the sequence with intensity scaled relative to the predefine “max1_LED#” powers (see below)

-	When *b* is entered, the same stimulus sequence will be played, but this time at the intensities defined by “max2_LED#” powers (see below)

-	If *0* is entered during a stimulus sequence, all LEDs will be turned off and all loop countered will be reset.

-	Further commands can easily be programmed by the user from the “Main Loop” part of the Arduino code.

It is important to note that the stimulation will only be played if a blanking signal is sent to the board.

Important to note, obviously the stimulation will only be played if a blanking signal is sent to the board.

***

## Calibrating the Stimulator

<p align="justify">Stimulating LEDs can be approximately brought into a desired intensity regime by adding a serial resistor to limit the current they receive (c.f. 5.2). They can also be further calibrated within the code:

<p align="justify">The TLC5947 is a 12-bit PWM grayscale driver, meaning that it offers up to 4,096 grey levels to adjust each LED power.

<p align="justify">On the Arduino code there is a second tab called “LED_values” which hard-codes the maximum power an LED can get. Those values range from 0 (no current) to 4095 (max current, 15 mA by default with potentiometer tuned all the way down).

<p align="justify">On the default script we defined two distinct max values (max1 & max2) that can be called individually. The purpose here is to have the opportunity to use the same stimulus sequence at two different regimes of light intensities. More can be added manually by the user. </p>

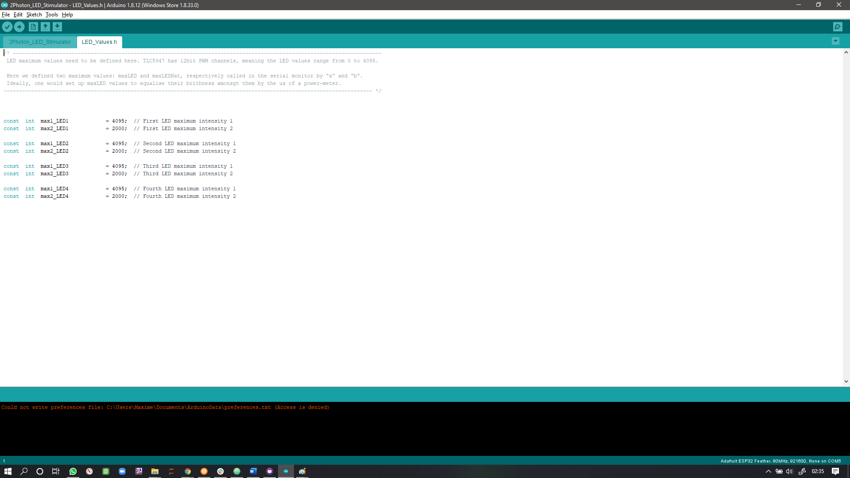
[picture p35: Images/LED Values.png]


<p align="justify">For the calibration, we suggest setting the max_LED# value to 4095 (full power) and use successively a spectrometer and a powermeter to adjust the LED brightness by finely turning the trimmer potentiometer at the back of the stimulator.

<p align="justify">As the LED output is linear relative to the values entered here (Fig. 3), any max_LED# value will be proportional to the LED power set up for the 4095 value. The LED value (0-100%) entered in the stimulus sequence is linearly mapped to 0-max_LED#.</p>

We also provide a calibration script in the form of an [iPyhton jupyter notebook](https://github.com/BadenLab/LED-Zappelin/blob/master/Instruction%20Manual/Stimulator%20Calibration/Stimulator_Calibration.ipynb). This script was designed to calibarte a 4 LEDs system for experiment on the zebrafish retina.

### Visual Stimulator Calibration

For the visual stimulator, we used the [ThorLabs Compact CCD Spectrometer](https://www.thorlabs.com/newgrouppage9.cfm?objectgroup_ID=3482) CCS200/M in combination with the [ThorLabs OSA software](https://www.thorlabs.com/software_pages/ViewSoftwarePage.cfm?Code=OSA).
We placed the spectrometer fiber patch cable at the sample position and played the calibration code on the stimulator. This calibration sequence plays each LED individually from 0 to 100% for 1 second and loops 5 times. This stimulus sequence is quite tedious so we encourage users to adapt it to their needs.
Recordings were made using the inbuilt trigger mode of the spectrometer (connected to the stimulator trigger output). We used an integration time of 1 second and applied the inbuilt spectrum correction in the OSA software. Data was extracted as .csv files and analysed using our [iPython analysis script](https://github.com/BadenLab/LED-Zappelin/blob/master/Instruction%20Manual/Stimulator%20Calibration/Stimulator_Calibration.ipynb).

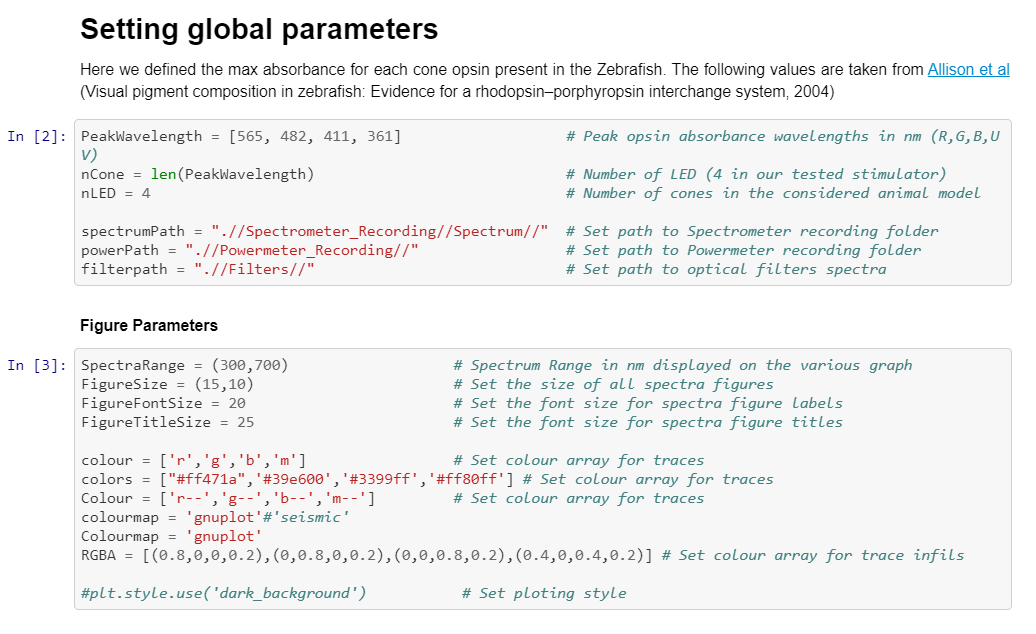
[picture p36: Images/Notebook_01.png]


For analysis purposes, we designed an [iPython notebook](https://jupyter.readthedocs.io/en/latest/install.html).
In this script, one has to first modify the global parameters:
  - Opsin maximum absorbance: *PeakWavelength* This array contains the peak asorbance for each opsin considered. For the zebrafish, we use the value defined by [Allison et al, 2004 - Visual pigment composition in Zebrafish](https://github.com/BadenLab/LED-Zappelin/blob/master/References/Allison%202004%20-%20Visual%20pigment%20composition%20in%20zebrafish.pdf)
  - Number of LEDs to be considered
  - Figure parameters: Figure sizes, spectra range to considered, etc.

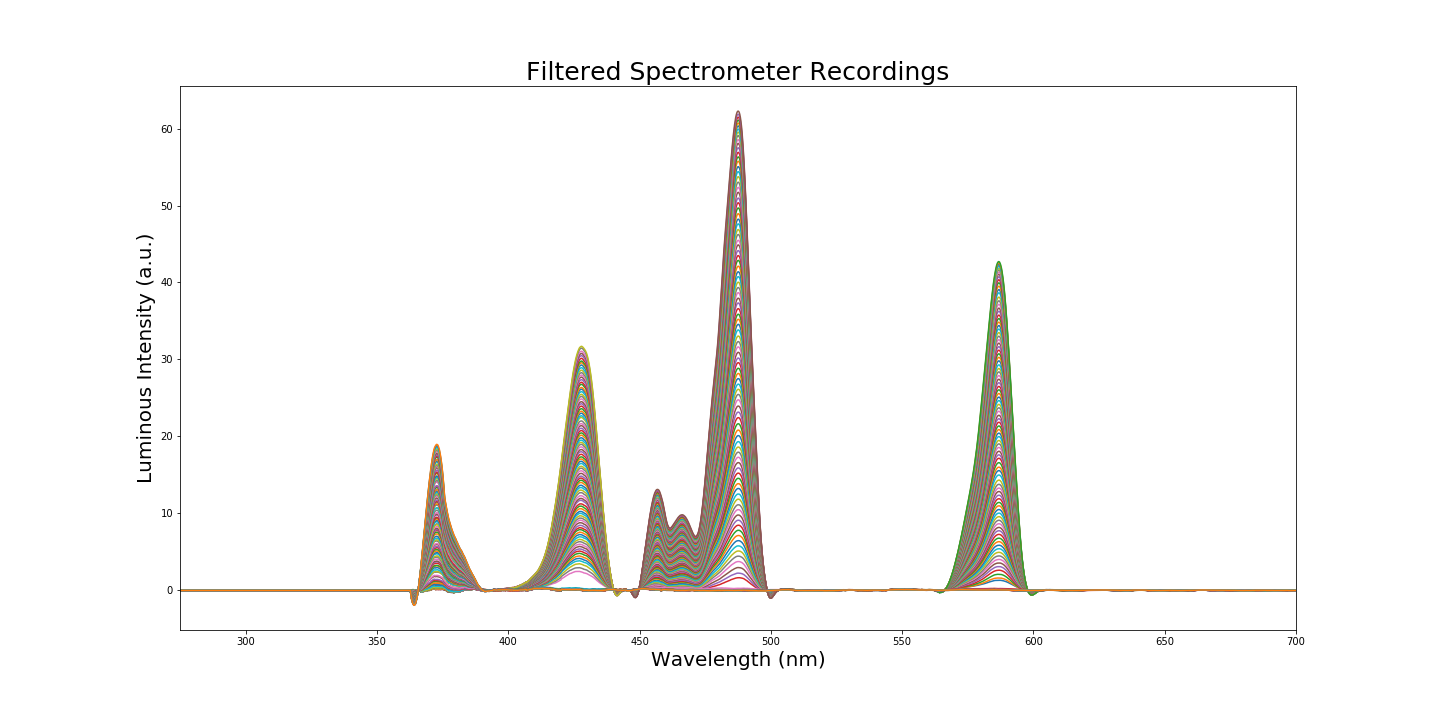
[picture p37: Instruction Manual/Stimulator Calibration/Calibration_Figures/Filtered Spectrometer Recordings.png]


.

.

The script then run a couple of slides to extract and smooth (Savitzky–Golay filter) the recording data.

From this recording, the peak wavelength of each LED is extracted and assigned to the *Peaks[ ]* array.

|                     |   Red LED  |  Green LED |  Blue LED  |   UV LED   |
| --------------------|:----------:|:----------:|:----------:|:----------:|
| Peak Wavelength (nm)|    586.9   |    487.5   |    427.9   |    372.8   |

Depending on the LEDs used or on the extra resistors that a user might want to connect in series to substantially tune down the LEDs, a powermeter shall be used to bring the LEDs to their desired max values. Here we suggest to set the potentiometers at mid-range and replace the spectrometer sensor by the powermeter's. In our case, we used a [ThorLabs Digital Handheld Optical Power](https://www.thorlabs.de/newgrouppage9.cfm?objectgroup_id=3341) coupled with a [ThorLabs Photodiode Power Sensor S130VC](https://www.thorlabs.de/thorproduct.cfm?partnumber=S130VC), 200 - 1100 nm, 50 mW. Each LED is then successively brought to their desired maximum power (here 40nW) and the powermeter configured to the LED peak wavelengths (λmax). Once this value has been reached, the *max_LED* value in the LED Values part of the Arduino code has to be decreased until a change is oberved. The max_LED value is then hard-coded and fine tuning can be achieved with the potentiometers.
At this stage, one might retake measurements with the spectrometer with this new power (in our case equalised amongst LEDs), and rerun the first part of this script to obtain more precise curves.

<p align="justify">To establish the LEDs performance we then plotted their normalised intensities (LED relative brightness) against the PWM (*array_LED#*) used in the Arduino code to drive them. A Linear fit along with the Sum of Square Error (SSE), demonstrates that the TLC5947 LED driver controls the LED in an optimal linear manner.</p>

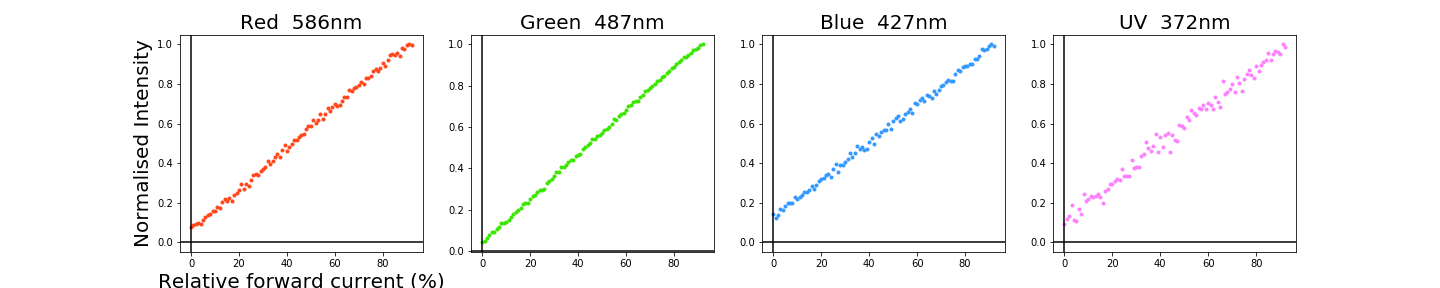
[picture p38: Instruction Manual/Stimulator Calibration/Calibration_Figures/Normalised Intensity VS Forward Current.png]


***

We then used the absorbance spectrum fitting template for visual pigment defined by [Govardoskii et al, 2000 - In Search of Visual Pigment Template](https://github.com/BadenLab/LED-Zappelin/blob/master/References/Govardovskii%202000%20-%20In%20search%20of%20the%20visual%20pigment%20template.pdf). Using the Opsin maximal absorbance defined earlier, this nomogram template describes the predicted shape of the absorbance spectra of all visual pigment. Here we obtained the following specra for the zebrafish cone photoreceptors that we plotted along the human visible spectrum as comparison.

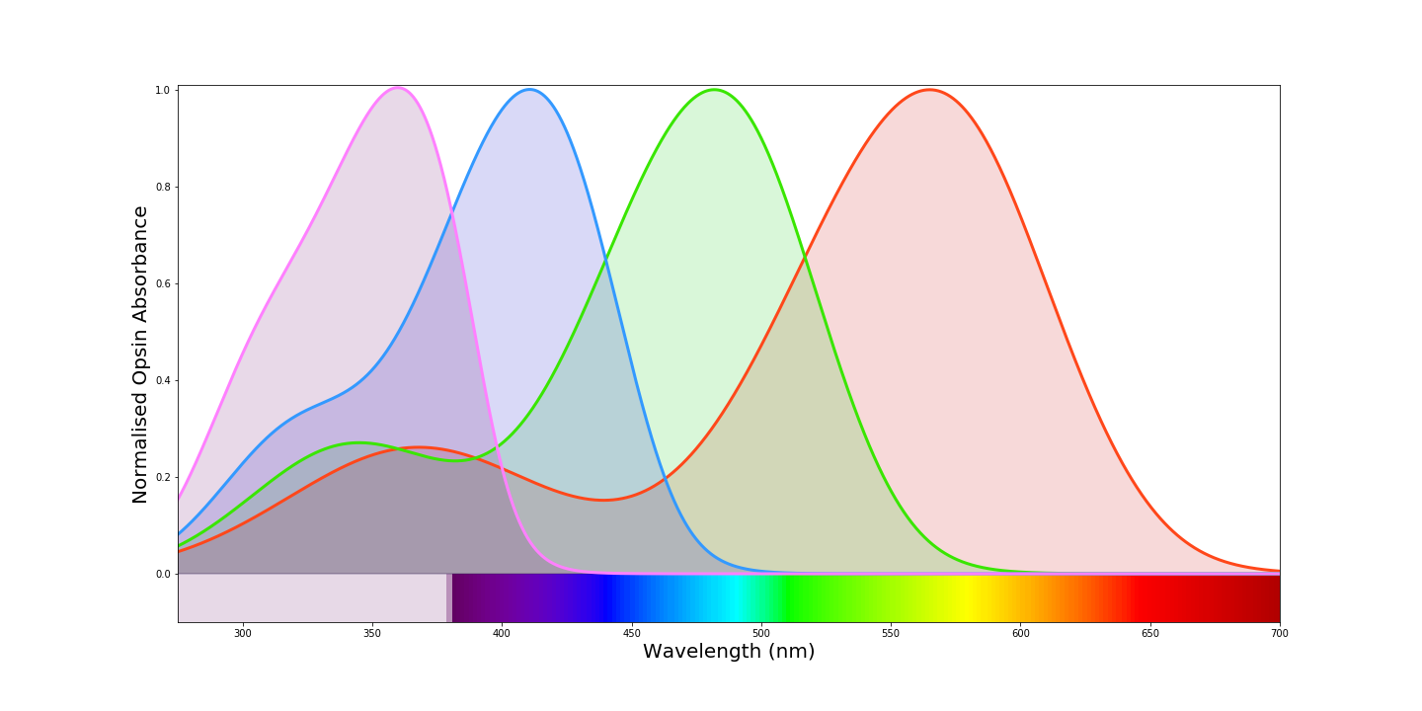
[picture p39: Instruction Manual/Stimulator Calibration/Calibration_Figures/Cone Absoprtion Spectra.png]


***

<p align="justify">Using the same display we plotted the LEDs spectra that we obtained from the spectrometer recordings.

<p align="justify">Then, we plotted the LED spectra along the cone opsin absorbance, and each LED’s spectral cross-section with respective target conein solid colours. Grey boxes indicate the positions of the two PMT detector bands. The Red-LED’s long-wavelength emission spectrum was chosen to limit spectral overlap with the red-fluorescence detection channel. Any loss in excitation efficiency of the red opsin was compensated for by increasing this LED’s power accordingly. </p>

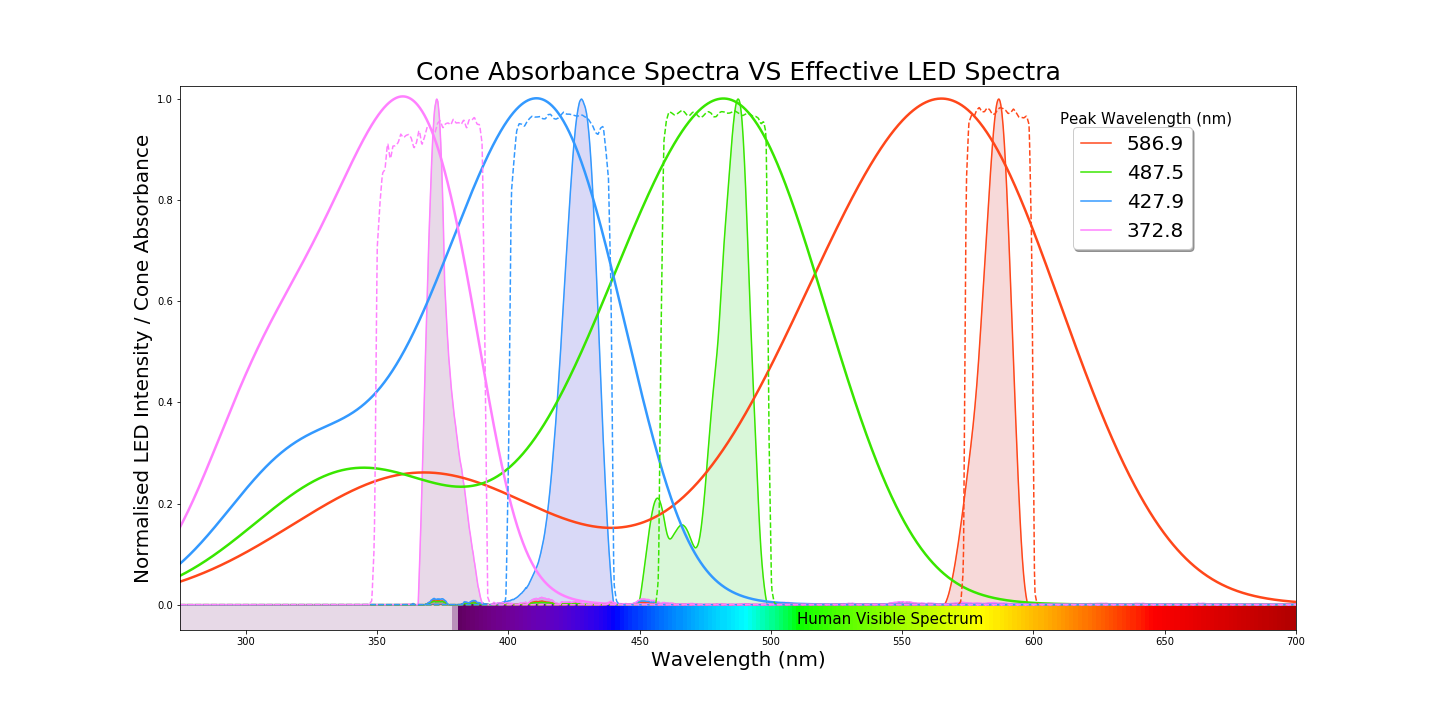
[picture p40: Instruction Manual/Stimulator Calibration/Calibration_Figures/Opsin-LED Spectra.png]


***

With the previous spectra, we estimate the relative co-excitation of photoreceptors by the LEDs:
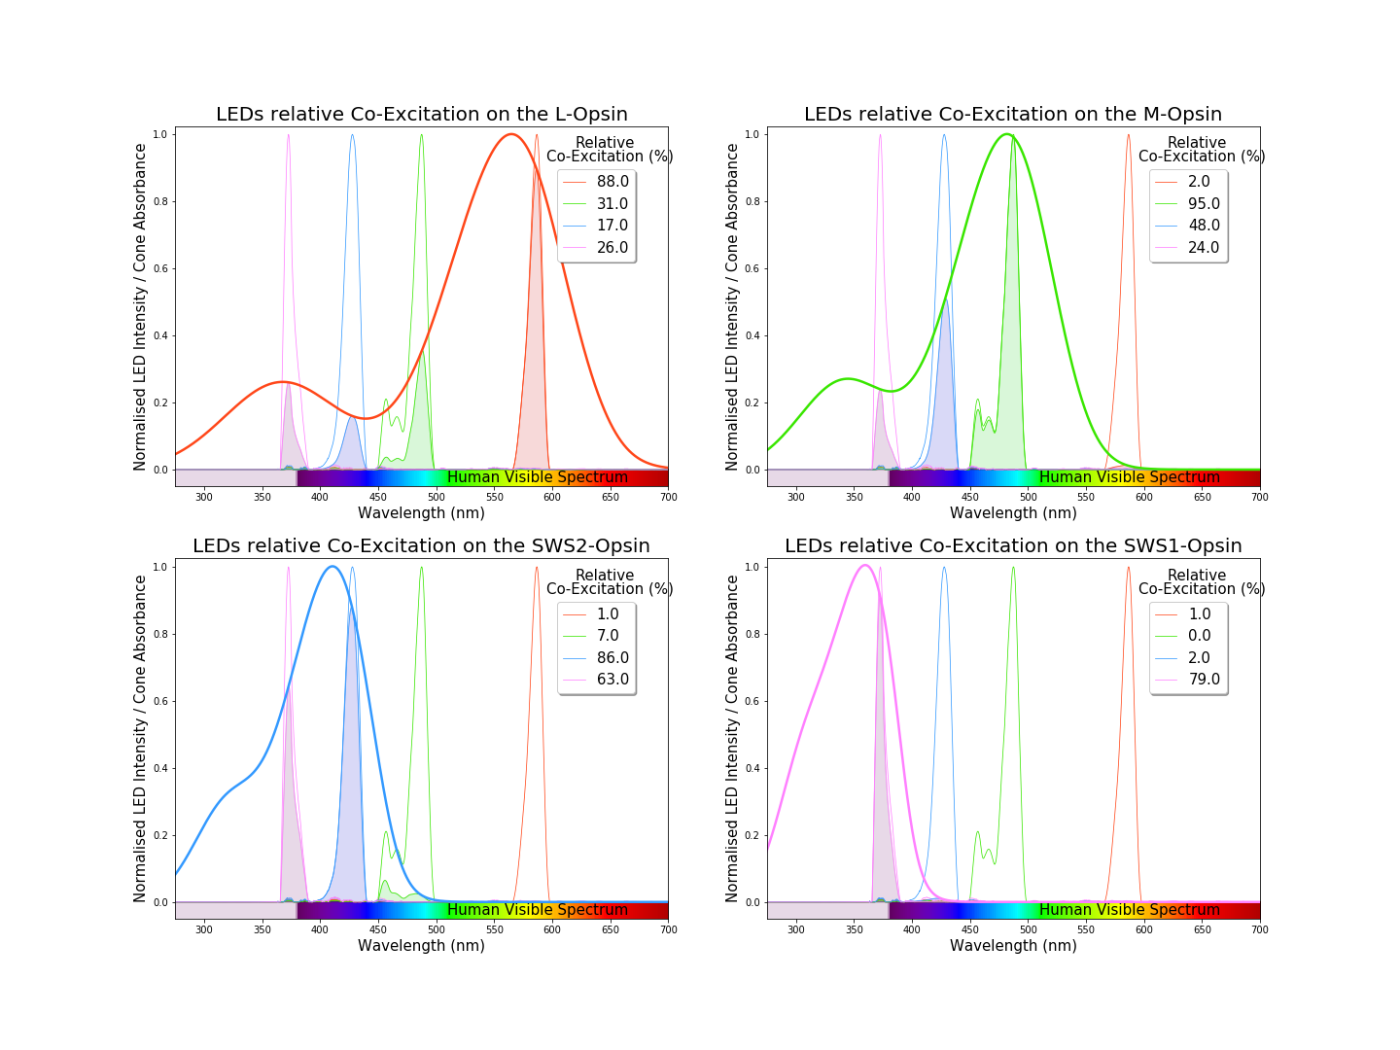
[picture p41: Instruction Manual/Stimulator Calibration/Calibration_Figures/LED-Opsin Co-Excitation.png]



***

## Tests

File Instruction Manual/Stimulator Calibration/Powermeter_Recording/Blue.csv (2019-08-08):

Optical Power Monitor
1.1.2315.102
Delimiter Used:
Start of Measurement | 8/6/2019 18:34:16
Sample Interval | 1 s
 | PM100D 18112641
Type | PM100D
Serialnumber | P0009872
Sensor | S130VC
SensorSerialnumber | 18112641
Wavelength / Responsivity | 427 nm
 |  |  | PM100D 18112641 | PM100D 18112641
Samples | Date (MM/dd/yyyy) | Time of day (hh:mm:ss) | Power (W) | Irradiance (W/cm²)
0 | 8/6/2019 | 18:34:16 | 9.8015E-11 | 1.3828E-10
1 | 8/6/2019 | 18:34:17 | -5.2799E-13 | -7.4489E-13
2 | 8/6/2019 | 18:34:18 | 4.1571E-12 | 5.8648E-12
3 | 8/6/2019 | 18:34:19 | -1.0294E-12 | -1.4523E-12
4 | 8/6/2019 | 18:34:20 | 5.1839E-11 | 7.3135E-11
5 | 8/6/2019 | 18:34:21 | -1.0566E-11 | -1.4906E-11
6 | 8/6/2019 | 18:34:22 | -1.1372E-11 | -1.6043E-11
7 | 8/6/2019 | 18:34:23 | -5.0191E-13 | -7.0809E-13
8 | 8/6/2019 | 18:34:24 | 1.1453E-12 | 1.6158E-12
9 | 8/6/2019 | 18:34:25 | 7.0013E-12 | 9.8773E-12
10 | 8/6/2019 | 18:34:26 | 2.8155E-10 | 3.9721E-10
11 | 8/6/2019 | 18:34:27 | 6.8543E-10 | 9.67E-10
12 | 8/6/2019 | 18:34:28 | 1.0813E-09 | 1.5255E-09
13 | 8/6/2019 | 18:34:29 | 1.5019E-09 | 2.1189E-09
14 | 8/6/2019 | 18:34:30 | 1.9337E-09 | 2.7281E-09
15 | 8/6/2019 | 18:34:31 | 2.3108E-09 | 3.26E-09
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

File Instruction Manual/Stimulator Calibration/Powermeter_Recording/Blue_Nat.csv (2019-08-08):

Optical Power Monitor
1.1.2315.102
Delimiter Used:
Start of Measurement | 8/6/2019 18:36:21
Sample Interval | 1 s
 | PM100D 18112641
Type | PM100D
Serialnumber | P0009872
Sensor | S130VC
SensorSerialnumber | 18112641
Wavelength / Responsivity | 427 nm
 |  |  | PM100D 18112641 | PM100D 18112641
Samples | Date (MM/dd/yyyy) | Time of day (hh:mm:ss) | Power (W) | Irradiance (W/cm²)
0 | 8/6/2019 | 18:36:21 | 5.3849E-11 | 7.597E-11
1 | 8/6/2019 | 18:36:22 | 5.6524E-11 | 7.9744E-11
2 | 8/6/2019 | 18:36:23 | 1.1686E-11 | 1.6487E-11
3 | 8/6/2019 | 18:36:24 | 2.2393E-11 | 3.1592E-11
4 | 8/6/2019 | 18:36:25 | 1.8146E-12 | 2.5601E-12
5 | 8/6/2019 | 18:36:26 | 2.2226E-11 | 3.1356E-11
6 | 8/6/2019 | 18:36:27 | 1.3192E-11 | 1.8611E-11
7 | 8/6/2019 | 18:36:28 | -1.0296E-12 | -1.4526E-12
8 | 8/6/2019 | 18:36:29 | 1.1351E-11 | 1.6014E-11
9 | 8/6/2019 | 18:36:30 | 1.9549E-11 | 2.758E-11
10 | 8/6/2019 | 18:36:31 | -1.1972E-12 | -1.689E-12
11 | 8/6/2019 | 18:36:32 | -2.5354E-12 | -3.5769E-12
12 | 8/6/2019 | 18:36:33 | 1.9814E-12 | 2.7954E-12
13 | 8/6/2019 | 18:36:34 | 8.6741E-12 | 1.2237E-11
14 | 8/6/2019 | 18:36:35 | 9.8453E-12 | 1.389E-11
15 | 8/6/2019 | 18:36:36 | 7.3589E-11 | 1.0382E-10
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

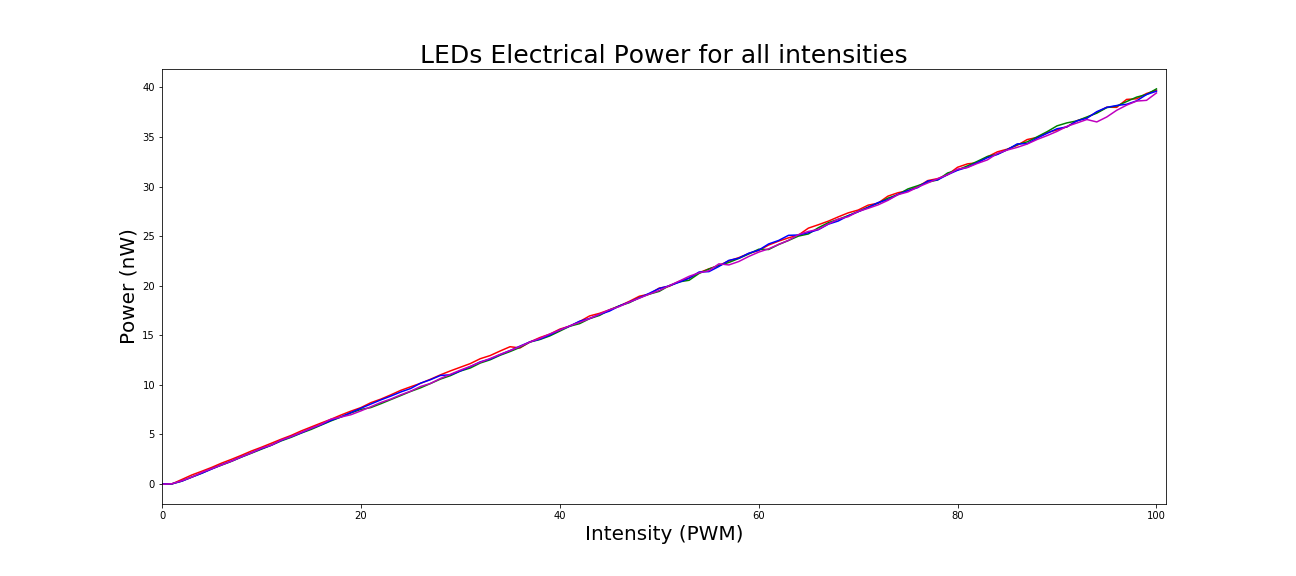
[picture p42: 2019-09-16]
Instruction Manual/Stimulator Calibration/Calibration_Figures/Powermeter Recordings.png

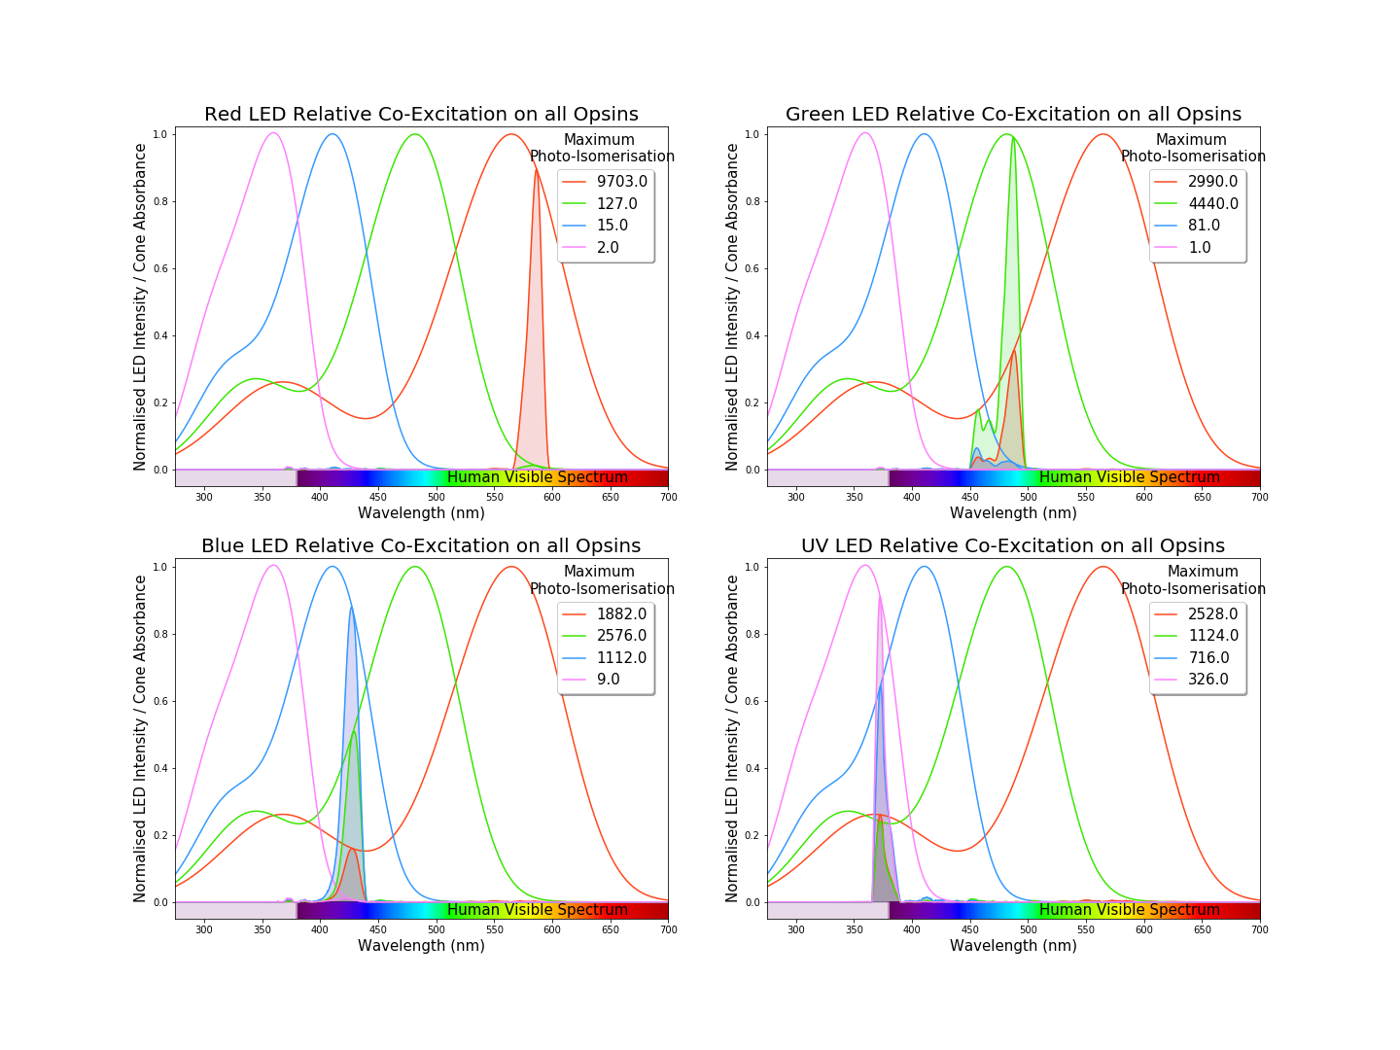
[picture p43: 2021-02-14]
Instruction Manual/Stimulator Calibration/Calibration_Figures/LED-Opsin Photo-Isomerisation Rates Nat-Stat.png

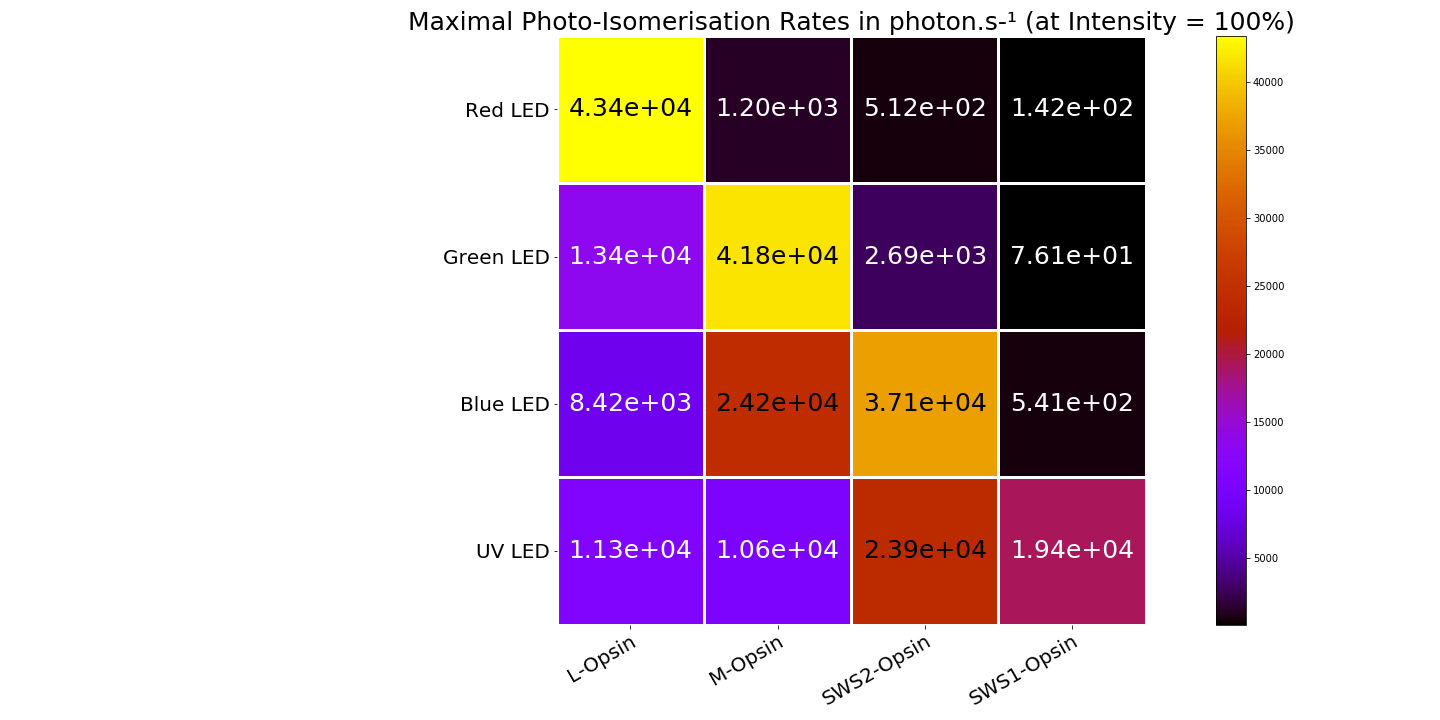
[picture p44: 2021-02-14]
Instruction Manual/Stimulator Calibration/Calibration_Figures/Photo-Isomerisation Rates Matrix.png

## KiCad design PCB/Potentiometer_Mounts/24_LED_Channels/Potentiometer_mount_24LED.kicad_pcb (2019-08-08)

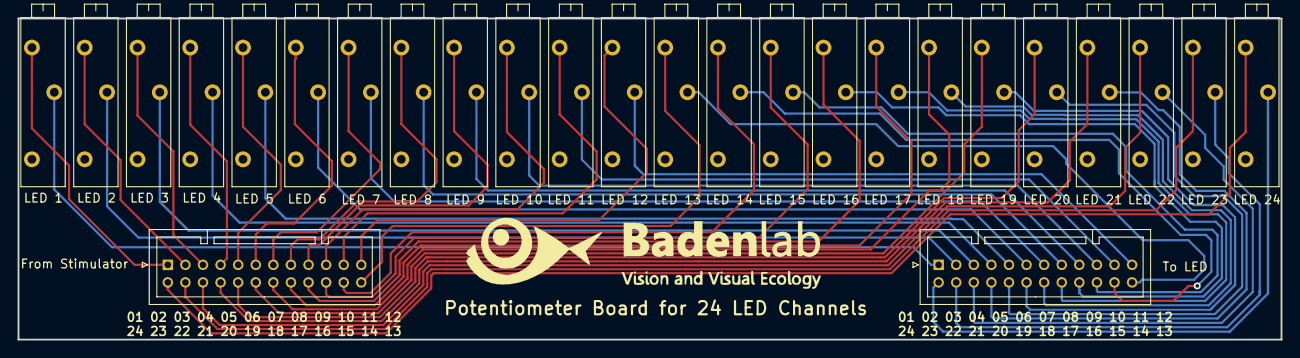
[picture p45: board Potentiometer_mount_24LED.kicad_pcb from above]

Board: 2 copper layers, 143.6 x 36.5 mm, 26 parts (0 on the bottom side), 48 nets.

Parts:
 LED 11: R_POT_TRIM; Potentiometer_Vishay_43_Horizontal
From Stimulator: JST_PUD_B24B-PUDSS_2x12_P2.00mm_Vertical
LED 1, LED 2, LED 3, LED 4: Potentiometer_Vishay_43_Horizontal
LED 5, LED 6, LED 7, LED 8, LED 9, LED 10, LED 12, LED 13, LED 14, LED 15, LED 16, LED 17, LED 18, LED 19, LED 20, LED 21, LED 22, LED 23, LED 24: R_POT_TRIM; Potentiometer_Vishay_43_Horizontal
To LED: JST_PUD_B24B-PUDSS_2x12_P2.00mm_Vertical

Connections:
unnamed: From Stimulator.1, LED 1.3
unnamed: From Stimulator.2, LED 2.3
unnamed: From Stimulator.3, LED 3.3
unnamed: From Stimulator.4, LED 4.3
unnamed: From Stimulator.5, LED 5.3
unnamed: From Stimulator.6, LED 6.3
unnamed: From Stimulator.7, LED 7.3
unnamed: From Stimulator.8, LED 8.3
unnamed: From Stimulator.9, LED 9.3
unnamed: From Stimulator.10, LED 10.3
unnamed: LED 11.3, From Stimulator.11
unnamed: From Stimulator.12, LED 12.3
unnamed: From Stimulator.13, LED 13.3
unnamed: From Stimulator.14, LED 14.3
unnamed: From Stimulator.15, LED 15.3
unnamed: From Stimulator.16, LED 16.3
unnamed: From Stimulator.17, LED 17.3
unnamed: From Stimulator.18, LED 18.3
unnamed: From Stimulator.19, LED 19.3
unnamed: From Stimulator.20, LED 20.3
unnamed: From Stimulator.21, LED 21.3
unnamed: From Stimulator.22, LED 22.3
unnamed: From Stimulator.23, LED 23.3
unnamed: From Stimulator.24, LED 24.3
unnamed: LED 1.2, To LED.1
unnamed: LED 2.2, To LED.2
unnamed: LED 3.2, To LED.3
unnamed: LED 4.2, To LED.4
unnamed: LED 5.2, To LED.5
unnamed: LED 6.2, To LED.6
unnamed: LED 7.2, To LED.7
unnamed: LED 8.2, To LED.8
unnamed: LED 9.2, To LED.9
unnamed: LED 10.2, To LED.10
unnamed: LED 11.2, To LED.11
unnamed: LED 12.2, To LED.12
unnamed: LED 13.2, To LED.13
unnamed: LED 14.2, To LED.14
unnamed: LED 15.2, To LED.15
unnamed: LED 16.2, To LED.16
unnamed: LED 17.2, To LED.17
unnamed: LED 18.2, To LED.18
unnamed: LED 19.2, To LED.19
unnamed: LED 20.2, To LED.20
unnamed: LED 21.2, To LED.21
unnamed: LED 22.2, To LED.22
unnamed: LED 23.2, To LED.23
unnamed: LED 24.2, To LED.24

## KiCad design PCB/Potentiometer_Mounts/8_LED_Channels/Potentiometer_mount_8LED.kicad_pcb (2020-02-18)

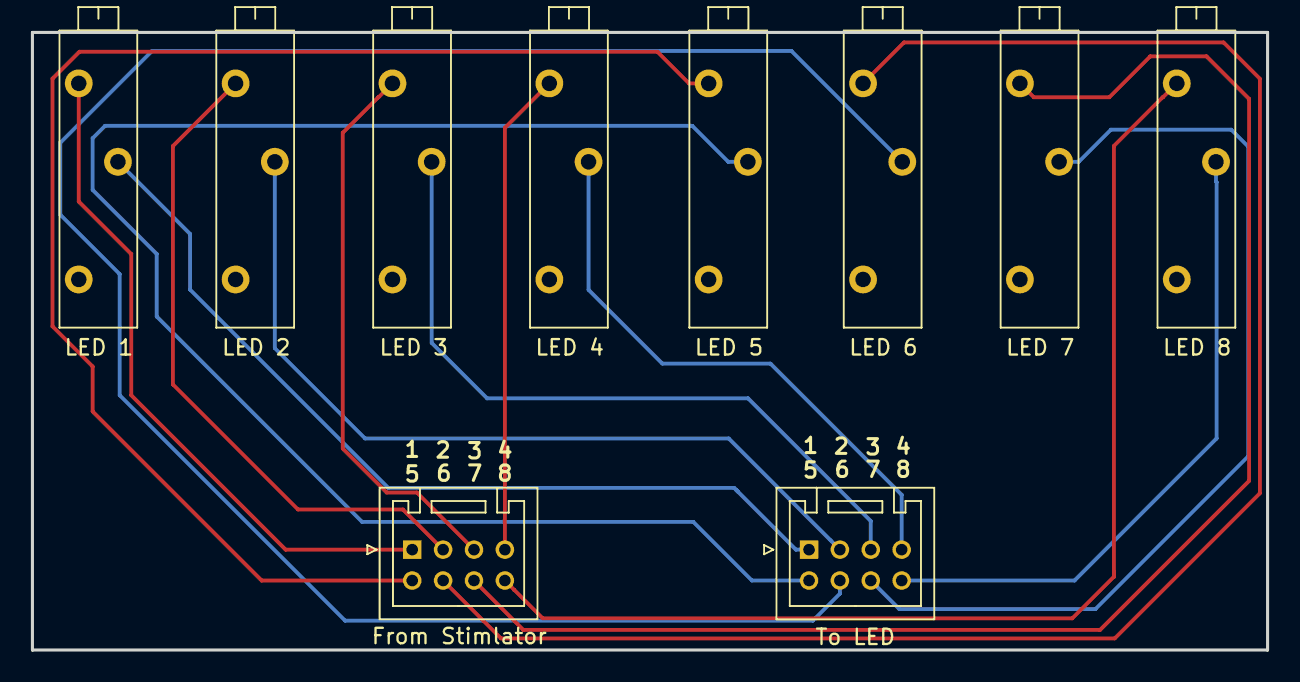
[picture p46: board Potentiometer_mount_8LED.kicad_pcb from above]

Board: 2 copper layers, 80.0 x 40.0 mm, 10 parts (0 on the bottom side), 8 nets.

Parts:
From Stimlator: JST_PUD_B08B-PUDSS_2x04_P2.00mm_Vertical
LED 1, LED 2, LED 3, LED 4, LED 5, LED 6, LED 7, LED 8: Potentiometer_Vishay_43_Horizontal
To LED: JST_PUD_B08B-PUDSS_2x04_P2.00mm_Vertical

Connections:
unnamed: From Stimlator.1, LED 1.3
unnamed: From Stimlator.3, LED 2.3
unnamed: From Stimlator.5, LED 3.3
unnamed: From Stimlator.7, LED 4.3
unnamed: LED 1.2, To LED.1
unnamed: LED 2.2, To LED.3
unnamed: LED 3.2, To LED.5
unnamed: LED 4.2, To LED.7

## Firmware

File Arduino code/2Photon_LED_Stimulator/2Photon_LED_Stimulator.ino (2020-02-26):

/* 
 
        LED Zappelin' is an open hardware LED stimulator that can individually
control up to 24 LEDs.

This Arduino file is designed to be uploaded on an Adafruit_HUZZAH ESP32 Feather or an Arduino Nano
Source : https://github.com/BadenLab/LED-Zappelin
The script relies on an incoming blanking signal, generated by a TTL, which updates the LEDs.
The stimulus speed has to be adjusted to the scan logic (scanning mirrors speed that corresponds to 
the blanking signal generated by the TTL): 1kHz/1ms, 500Hz/2ms, etc.
A trigger signal is generated at the begining of the stimulus and then every 1.0 seconds.

Library "Adafruit TLC5947" needs to be installed.
 
The default script is parametered for 4 LEDs (connected to pin 0 to 3), and their respective proxy LEDs 
(connected to pin 4 to 7)


This project is Open Source licensed, released under CERN OHL v1.2

by  M.J.Y. Zimmermann, 2019.02.05
Baden Lab, CRPC, School of Life Sciences, University of Sussex, United Kingdom
*/


/* ------------------------------------------------------------------------------------
                           Stimulus parameters
-------------------------------------------------------------------------------------*/                                                                                             

int           nLoops           = 500;     //  Number of repeats of the arrays (i.e. Loops)
const int     nArrayEntries    = 3;       //  Number of entries in the arrays, including preadaption at position 0
const int     Scan_Logic       = 2;       //  Scanning logic (1 for 1ms scans, 2 for 2ms scans, etc.)



// // // // // // // // // // // // // // // // // // // // // // // // // // //
// // // // // // // // // STIMULUS SEQUENCE START // // // // // // // // // //
// // // // // // // // // // // // // // // // // // // // // // // // // // // 

// The array_LED# values are expressed in percentage and should only be expressed from 0-100
const int8_t array_LED1[] PROGMEM = {
0,100,0
};
const int8_t array_LED2[] PROGMEM = {    
0,100,0
};
const int8_t array_LED3[] PROGMEM = {    
0,100,0
};
const int8_t array_LED4[] PROGMEM = {
0,100,0
};

// The array_Time values are expressed in milliseconds
const int16_t array_Time[] PROGMEM = {      
5000,1000,1000
};

// // // // // // // // // // // // // // // // // // // // // // // // // // //
// // // // // // //  STIMULUS SEQUENCE END  // // // // // // // // // // // //
// // // // // // // // // // // // // // // // // // // // // // // // // // //


/* ------------------------------------------------------------------------------------
                           Microcontroller Board Selection
-------------------------------------------------------------------------------------*/

      //#define Arduino_Nano
      #define Adafruit_ESP32

      
/* ------------------------------------------------------------------------------------
                    Internal Definitions (Change at your own risk)
-------------------------------------------------------------------------------------*/

#include "LED_Values.h"                     // Include LED Values defined in the second tab
#include <SPI.h>                            // Include the arduino serial port interface library
#include "Adafruit_TLC5947.h"               // Include the Adafruit TLC5947 libvrary. For better result one may change the number of channel defined in the Adafruit_TLC5947.cpp library


#ifdef Arduino_Nano
    #define   data            4             // SPI connection, DIN connected to pin D4
    #define   clock           5             // SPI connection, CLK connected to pin D5
    #define   latch           6             // SPI connection, LAT connected to pin D6
    //#define   oe              2           // Optional feature to prevent LED to light up when powering up the TLC board connected to pin D2
    const int      pSyncOut      =   A0;    // Trigger channel must be connected to pin A0
    const int      pBlank        =   3;     // Blanking signal channel must be connected to pin D3
#endif

#ifdef Adafruit_ESP32
    #define   data           18             // SPI connection, DIN connected to pin MOSI/18
    #define   clock           5             // SPI connection, CLK connected to pin SCK/5
    #define   latch          21             // SPI connection, LAT connected to pin 21
    //#define   oe            25            // Optional feature to prevent LED to light up when powering up the TLC board connected to pin A1/DAC1
    const int      pSyncOut      =   26;    // Trigger channel must be connected to pin A0/DAC2
    const int      pBlank        =   36;    // Blanking signal channel must be connected to pin A4/36
#endif

    Adafruit_TLC5947 tlc = Adafruit_TLC5947(1, clock, data, latch);

    

/* Global variables */  
char           sCmd;                        // Serial monitor 
int            i;                           // iteration loop factor
word           BaudRate      = 115200;      // Baud Rate
int            led1          = 0;           // Define 1st Channel       
int            led2          = 1;           // Define 2nd Channel
int            led3          = 2;           // Define 3rd Channel
int            led4          = 3;           // Define 4th Channel
int            proxy_led1    = 4;           // Define 1st Channel marker        
int            proxy_led2    = 5;           // Define 2nd Channel marker
int            proxy_led3    = 6;           // Define 3rd Channel marker
int            proxy_led4    = 7;           // Define 4th Channel marker
  
/* Global LED variables */
volatile word   stled1;                     // First LED value   
volatile word   stled2;                     // Second LED value
volatile word   stled3;                     // Third LED value
volatile word   stled4;                     // Fourth LED value
word            array1[nArrayEntries];      // First LED Array
word            array2[nArrayEntries];      // Second LED Array
word            array3[nArrayEntries];      // Third LED Array
word            array4[nArrayEntries];      // Fourth LED Array

/* Timing variables */
volatile word  pulse;                                             // Pulse number
word           Time[nArrayEntries];                               // Time Array
float          x_Logic            =   1.0/Scan_Logic;             // Factor applied to the timing according to the scanning logic

/* Trigger variables */
int     Trigger_Duration            =   25;                       // Length of the Trigger signal in ms
int     TriggerCounter_Duration     =   1000;                     // Lenght of the Trigger loop in ms
word    Trigger_dur        =   Trigger_Duration * x_Logic;        // Trigger signal duration adjusted
word    TriggerCounter_dur =   TriggerCounter_Duration * x_Logic; // Trigger loop duration adjusted  
    
/* Reset Parameters */
volatile word  iLoop                = 0;       // Actual loop number = iLoop + 1
volatile word  PulseCount           = 0;       // Count the number of pulses delivered by the blanking signal
volatile int   PulseCount_Trigger   = 0;       // Count the number of pulses generated for the trigger channel (A0 pin)
volatile int   ArrayPosition        = 0;       // Position array within the current loop

/* Flags */
bool   SettingFlag   =  true;
bool   BlankingFlag  =  true;


/* -----------------------------------------------------------------------------------
                                 Internal methods
 ------------------------------------------------------------------------------------*/

void setup(){

// Initialise the serial communication with PC
  Serial.begin(BaudRate);

// Initialise the Adafruit TLC driver 
  tlc.begin();
  tlc.write();  

// Set pins
  pinMode(pSyncOut, OUTPUT);  
  digitalWrite(pSyncOut, LOW);  
  pinMode(pBlank, INPUT);
  digitalWrite(pBlank, HIGH);
}

/* ----------------------------------------------------------------------------------*/
/* -------------------------------- Turn all LED off --------------------------------*/

void Play0(){
      tlc.setPWM(led1,0);                                // Set First LED to 0
      tlc.setPWM(led2,0);                                // Set Second LED to 0
      tlc.setPWM(led3,0);                                // Set Third LED to 0 
      tlc.setPWM(led4,0);                                // Set Fourth LED to 0
      tlc.setPWM(proxy_led1,0);                          // Set First proxy LED to 0
      tlc.setPWM(proxy_led2,0);                          // Set Second proxy LED to 0
      tlc.setPWM(proxy_led3,0);                          // Set Third proxy LED to 0 
      tlc.setPWM(proxy_led4,0);                          // Set Fourth proxy LED to 0
      tlc.write();   
      Serial.println("-> All LEDs off"); 
      
      PulseCount = 0;                                    // Reset Pulse counter
      PulseCount_Trigger = 0;                            // Reset Trigger pulse counter
      ArrayPosition = 0;                                 // Reset Array counter
      
      SettingFlag = true;                                // Return to initial condition
      BlankingFlag = true;                               // Return to initial condition
}



/* ----------------------------------------------------------------------------------*/
/* ------------------------------ Play Stimulus Array -------------------------------*/

void PlayArrays() {

/* Defining timing according to the current array position */
    pulse = Time[ArrayPosition];
    
/* Trigger ------------------------------------------------------------------------*/

    /* Keep Trigger on for the trigger duration */
    if(PulseCount_Trigger <= Trigger_dur && ArrayPosition > 0){
        PulseCount_Trigger += 1;                         // Trigger Pulse Counter, move to the next pulse
    } 
    /* Keep Trigger off for the rest of the trigger duration */
    if(PulseCount_Trigger > Trigger_dur && ArrayPosition > 0){
        digitalWrite(pSyncOut, LOW);                     // Turn Trigger off
        PulseCount_Trigger += 1;                         // Trigger Pulse Counter, move to the next pulse
    }

    /* Once Trigger duration is reached, reset counter and turn trigger on */
    if(PulseCount_Trigger == TriggerCounter_dur+1 && ArrayPosition > 0){
        PulseCount_Trigger = 0;                          // Reset Trigger pulse counter
        digitalWrite(pSyncOut, HIGH);                    // Turn Trigger on
    }
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

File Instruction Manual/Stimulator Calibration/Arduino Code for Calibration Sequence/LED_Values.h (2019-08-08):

/* -----------------------------------------------------------------------------------------------------------------------
 LED maximum values need to be defined here. TLC5947 has 12bit PWM channels, meaning the LED values range from 0 to 4095.

 Here we defined two maximum values: maxLED and maxLEDNat, respectively called in the serial monitor by "a" and "b".
 Ideally, one would set up maxLED values to equalise their brithness amonsgt them by the us of a power-meter.
----------------------------------------------------------------------------------------------------------------------- */



const  int  max1_LED1            = 4095;  // First LED maximum intensity
const  int  max2_LED1            = 2000;  // First LED minimum intensity

const  int  max1_LED2            = 4095;  // Second LED maximum intensity
const  int  max2_LED2            = 2000;  // Second LED minimum intensity

const  int  max1_LED3            = 4095;  // Third LED maximum intensity
const  int  max2_LED3            = 2000;  // Third LED minimum intensity

const  int  max1_LED4            = 4095;  // Fourth LED maximum intensity
const  int  max2_LED4            = 2000;  // Fourth LED minimum intensity

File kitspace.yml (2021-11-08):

multi:
  PCB/Stimulator:
    summary: A custom board to implement LED Zappelin', an opensource LED controller for 2-photon microscopy
    site: https://www.sciencedirect.com/science/article/pii/S2468067220300365
    color: green
    bom: PCB/Stimulator/1-click-bom.csv
    gerbers: PCB/Stimulator/gerber_files
    readme: README.md
  PCB/Potentiometer_Mounts/4_LED_Channels:
    summary: 4 LED channels option board for the LED Zappelin' project
    site: https://www.sciencedirect.com/science/article/pii/S2468067220300365
    color: green
    bom: PCB/Potentiometer_Mounts/4_LED_Channels/1-click-bom.csv
    gerbers: PCB/Potentiometer_Mounts/4_LED_Channels/gerber_files
    readme: README.md
  PCB/Potentiometer_Mounts/8_LED_Channels:
    summary: 8 LED channels option board for the LED Zappelin' project
    site: https://www.sciencedirect.com/science/article/pii/S2468067220300365
    color: green
    bom: PCB/Potentiometer_Mounts/8_LED_Channels/1-click-bom.csv
    gerbers: PCB/Potentiometer_Mounts/8_LED_Channels/gerber_files
    readme: README.md
  PCB/Potentiometer_Mounts/16_LED_Channels:
    summary: 16 LED channels option board for the LED Zappelin' project
    site: https://www.sciencedirect.com/science/article/pii/S2468067220300365
    color: green
    bom: PCB/Potentiometer_Mounts/16_LED_Channels/1-click-bom.csv
    gerbers: PCB/Potentiometer_Mounts/16_LED_Channels/gerber_files
    readme: README.md
  PCB/Potentiometer_Mounts/24_LED_Channels:
    summary: 24 LED channels option board for the LED Zappelin' project
    site: https://www.sciencedirect.com/science/article/pii/S2468067220300365
    color: green
    bom: PCB/Potentiometer_Mounts/24_LED_Channels/1-click-bom.csv
    gerbers: PCB/Potentiometer_Mounts/24_LED_Channels/gerber_files
    readme: README.md

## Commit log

2019-08-08 First upload 20190808
    [1_LED_Holder.stl, 2_LED_Holder.stl, 3_LED_Holder.stl, 4_LED_Holder.stl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]
2019-09-16 Update Supplementary Material.odt
2019-09-17 PCB update
    [Multi Chromatic Stimulator-B.Cu.gbr, Multi Chromatic Stimulator-B.Mask.gbr, Multi Chromatic Stimulator-B.Paste.gbr, Multi Chromatic Stimulator-B.SilkS.gbr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]
2019-10-24 update 24/10/2019
    [Multi Chromatic Stimulator-B.Cu.gbr, Multi Chromatic Stimulator-B.Mask.gbr, Multi Chromatic Stimulator-B.Paste.gbr, Multi Chromatic Stimulator-B.SilkS.gbr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]
2020-02-21 Update Arduino Code.png
2020-02-26 upload images
    [Optogenetics - Experimental setup.FCStd, Optogenetics - Mounting Chamber 1.FCStd, Optogenetics - Mounting Chamber 2.FCStd]
2020-02-26 Update 3D Designs
    [MultiChromatic Stimulator v2.1.scad]
2020-02-26 Update Arduino Code
2020-02-26 Update PCB
    [LED Zappelin-B.Adhes.gbr, LED Zappelin-B.CrtYd.gbr, LED Zappelin-B.Cu.gbr, LED Zappelin-B.Fab.gbr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]
2020-02-26 Create BOM - Stimulator.csv
    [BOM - Stimulator.csv]
2020-03-04 prepare files and folders for kitspace
    [LED Zappelin-B.Adhes.gbr, LED Zappelin-B.CrtYd.gbr, LED Zappelin-B.Cu.gbr, LED Zappelin-B.Fab.gbr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]
2020-08-01 Update BOM - Stimulator.csv
    [BOM - Stimulator.csv]
2020-08-01 correct naming conventions
    [Potentiometer_mount_16LED-B.Adhes.gbr, Potentiometer_mount_16LED-B.CrtYd.gbr, Potentiometer_mount_16LED-B.Cu.gbr, Potentiometer_mount_16LED-B.Fab.gbr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]
2020-08-01 rename 24 channel folder
    [1-click-bom.csv, Potentiometer_mount_24LED-B.Adhes.gbr, Potentiometer_mount_24LED-B.CrtYd.gbr, Potentiometer_mount_24LED-B.Cu.gbr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]
2020-08-04 Add readmes to kitspace.yml
    You can change these to seperate readmes for individual boards if you ever need to
2021-06-10 update 1 click bonm
    [1-click-bom.csv]
2021-11-08 Update README.md
    https://forum.kicad.info/t/warning-avoid-all-links-to-kicad-pcb-org-use-kicad-org/31521
